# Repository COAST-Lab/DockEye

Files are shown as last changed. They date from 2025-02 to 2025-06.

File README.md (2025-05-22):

# Open Fluorometer

## About

This is the repository for an in-development, open-source, low-cost fluorometer for measuring water quality parameters. The current objective is measuring chlorophyll-*a* and turbidity,
though more parameters may be added in the future. This sensor uses a cuvette-based approach, similar to benchtop spectrofluorometers, rather than a truly in-situ one. The advantage of this approach is the ability to control ambient light while not strictly needing to be waterproof. Samples can be collected from the surface by hand or at depth using a Van Dorn sampler or CTD-Rosette.

This sensor continues the research from the now-deprecated https://github.com/COAST-Lab/Low-Cost-Multiparameter-Water-Quality-Sensor built using the Particle Argon microcontroller. 
The new version uses an ESP32-S3, which uses the Arduino IDE rather than the Particle Workbench.

The MOORE Foundation's SOCON (Sustained Ocean Color Observations from Nanosatellites) program funds this project.

## Introduction

This sensor is built using an Adafruit ESP32-S3 Feather microcontroller, an Adafruit Adalogger/RTC, an AS7341 light sensor, an AW9523 LED driver, a 430 nm blue LED, a 910 nm NIR LED, and a 3D printed enclosure. 
This repository currently contains firmware for flashing to the microcontroller and 3D printable design models for the enclosure, and scripts for data analysis, etc. This sensor is in active development, and this repository will be updated continuously as progress is made. 

## Parts

A list of parts can be found here:

- [ESP32-S3 Microcontroller](https://www.adafruit.com/product/5477)
- [Adalogger Datalogger/RTC](https://www.adafruit.com/product/2922)
- [AW9523 LED Driver](https://www.adafruit.com/product/4886)
- [AS7341 Light Sensor](https://www.adafruit.com/product/4698)
- [Blue LED](https://www.thorlabs.com/thorproduct.cfm?partnumber=LED430L)
- [NIR LED](https://www.thorlabs.com/thorproduct.cfm?partnumber=LED910L)

Additional parts include a soldering iron, solder, wire, a breadboard, access to a 3D printer, an SD card, a USB-C data cable, and hardware for assembling the sensor. 

A glass or quartz cuvette will be needed for calibrating and running samples. Because the chlorophyll-*a* calibration procedure is completed in acetone, plastic cuvettes are not advised. Acetone can dissolve some plastics, although certain plastics may be incompatible. The glass cuvettes that we are currently using are rather inexpensive, and can be found on Amazon [here](https://www.amazon.com/Fluorescence-Spectrophotometer-Cuvettes-pathlength-Fluorometer/dp/B07YDZ6K2B?crid=TBT16WYR38HM&dib=eyJ2IjoiMSJ9.Rx6TjeI6e-pFg3Mv68xtz28ZP_Q9hPI-yeQDbd4sN2l0LnT0KrBOkWjchOp21-8up7uFRnGXH4NQ6EaVXD32cu2CRUydlVmxSTyXF9Sp9oGG_GkgRuUTdxTE_vuw7iFTRlXKrGBJVSP3u1wZ12FmtyhuNQ71NkWIS9Gg2aIDsoQEjo3d2ZUMWSBvYHaW4YlxplcTskGwRPYe4TKxq8esrUAnyXS-2K3-_TNK5aQQeNM.WDhcMW94lNpOqJgwk2HZfrtGYfncKdvNy5RRSyoP6e8&dib_tag=se&keywords=glass+cuvettes&qid=1747334719&sprefix=glass+cuvettes%2Caps%2C126&sr=8-8). Ensure that any cuvettes purchased are specifically for fluorometry (with four transparent sides) and not for spectrophotometers, as those only have two transparent sides. These are incompatible with this design, as the LEDs in this design are placed at a 90-degree angle from the light detector. 

3D print files can be found [here](https://github.com/COAST-Lab/Open-Fluorometer/tree/main/Hardware/Housing).

## Wiring Instructions

Instructions for assembly will be added soon. For now, here is a simple explanation on how to wire the parts together:

- Solder the included male headers onto the corresponding pins on the ESP-32
- Solder the stacking headers onto corresponding pins on the Adalogger
- Solder/insert (depending on type) pins into breadboard
- Add a jumper wire from 3.3V and GND to +/-
- Solder the following pins on the AW9523 to the corresponding pins on the ESP32-S3
  - VIN to +
  - GND to -
  - SCL to SCL
  - SDA to SDA
- Solder the following pins on the AS7341 to the corresponding pins on the ESP32-S3
  - VIN to +
  - GND to -
  - SCL to SCL
  - SDA to SDA
- Solder the Blue LED to + and AW9523 Pin 10
- Solder the NIR LED to + and AW9523 Pin 0

Instructions for mounting the LEDs and light sensor to the cuvette holder will be added soon.

## Data Analysis

Scripts for data analysis and data files can be found [here](https://github.com/COAST-Lab/Open-Fluorometer/tree/main/Data%20Analysis).

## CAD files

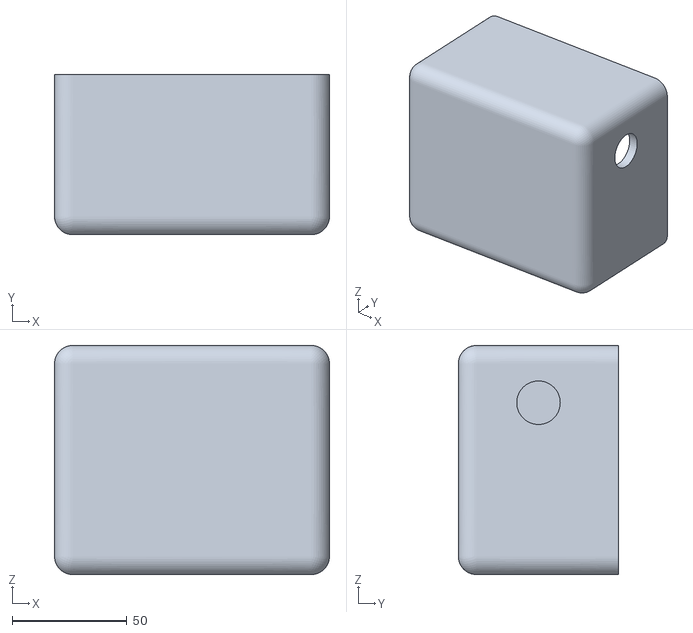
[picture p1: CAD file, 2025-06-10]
Hardware/Housing/Open-Fluorometer-Main-Housing v7.stl
120.0 x 70.0 x 100.0

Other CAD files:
Hardware/Housing/Open-Fluorometer-Main-Housing v9.stl
Hardware/Housing/Open-Fluorometer-Main-Housing v8.stl
Hardware/Housing/Open-Fluorometer-Lid v2.f3d
Hardware/Housing/Open-Fluorometer-Main-Housing v4.f3d

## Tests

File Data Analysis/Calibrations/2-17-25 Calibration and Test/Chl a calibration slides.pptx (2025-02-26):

## Chlorophyll-a calibration curve

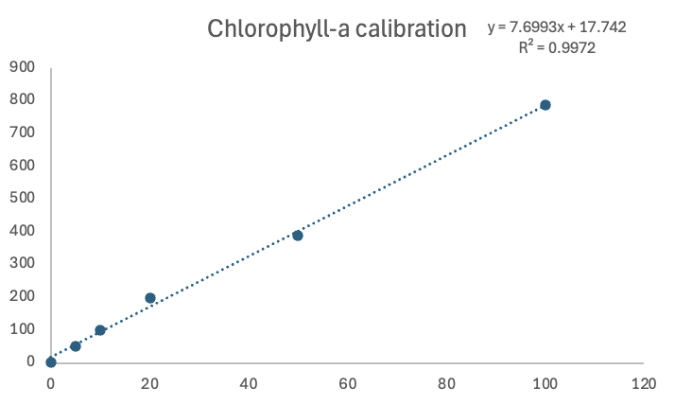
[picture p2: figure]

- Dilutions made from a stock solution measured at 297.7 ug/L
- Completed serial dilution from 100 to 5 ug/L in 90% acetone
- Vortexed stocks and standards before spiking

Concentration (ug/L) | Counts
100 | 788.625
50 | 389.1875
20 | 199.75
10 | 99.4375
5 | 50.75
0 | 3.0625

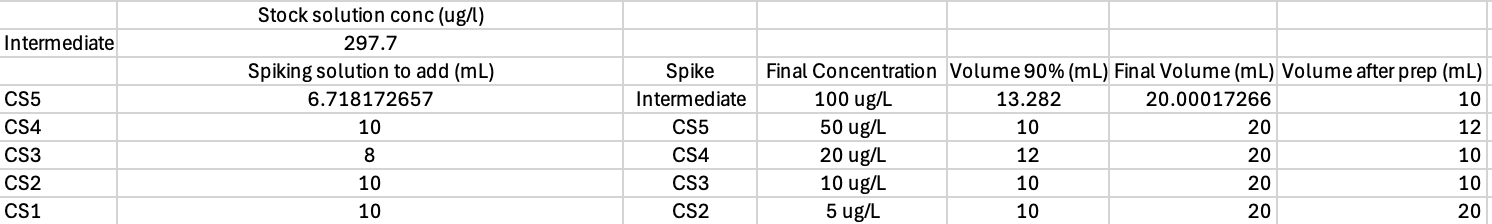
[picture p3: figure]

## Field validation test

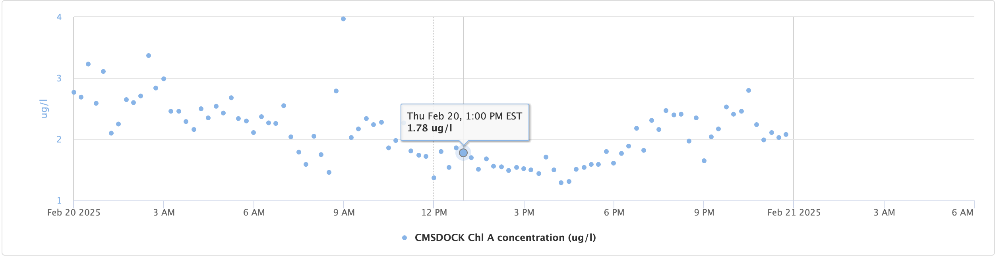
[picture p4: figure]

- Sampling location close to CORMP EXO2
- 1.78 ug/L measurement from CORMP
- Measurement taken on the surface in an amber bottle
  - CORMP measurements deeper
- 17.89 ug/L average on OF
  - Factor of 10 difference, calculation error or sensor issue?

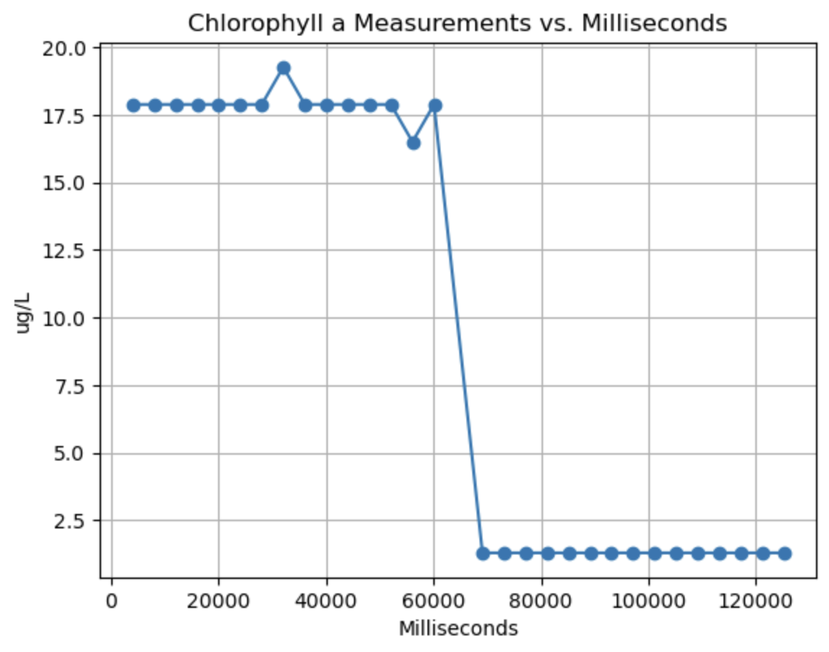
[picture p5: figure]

## Potential causes of discrepancy

- Calculations
  - Spreadsheet for trichromatic chlorophyll method may have calculation mistake
  - Problem with calibration curve calculations
  - Problem with python script
- Environmental factors
  - Acetone vs seawater
  - Photochemical quenching in seawater
  - EXO2 in a slightly different place at a different depth (slightly)
- Sensor sensitivity issue

## Solutions

1. Check all calculations again and have Phil double check them
2. Calibrate Dr. Loh’s Horiba and test standards on there to determine if it agrees with the spectrophotometer or the OF
3. Use Van Dorn sampler to sample in the same place and depth as the EXO2
4. Make chlorophyll standards using CMS highly filtered seawater rather than acetone

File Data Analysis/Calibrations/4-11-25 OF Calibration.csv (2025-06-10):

Date and Time | ASTEP | ATIME | GAIN | LED Status | LED Intensity | Test | Seconds | Milliseconds | Type | F1 (Basic) | F2 (Basic) | F3 (Basic) | F4 (Basic) | F5 (Basic) | F6 (Basic) | F7 (Basic) | F8 (Basic) | Clear (Basic) | NIR (Basic) | Type | F1 (Raw) | F2 (Raw) | F3 (Raw) | F4 (Raw) | F5 (Raw) | F6 (Raw) | F7 (Raw) | F8 (Raw) | Clear (Raw) | NIR (Raw) | Measurement Type
2104/5/32 (Monday) 30:7:22 | 999 | 255 | 9 | LED Status | LED Intensity | 6 | 21 | 21491 | BASIC COUNTS | 0 | 0 | 0 | 0 | 0 | 0 | 0 | 0 | 0 | 0 | RAW VALUES | 134 | 592 | 57 | 19 | 14 | 17 | 16 | 11 | 562 | 0 | chlorophyll a
2104/5/32 (Monday) 30:7:26 | 999 | 255 | 9 | LED Status | LED Intensity | 6 | 25 | 25481 | BASIC COUNTS | 0 | 0 | 0 | 0 | 0 | 0 | 0 | 0 | 0 | 0 | RAW VALUES | 131 | 589 | 57 | 20 | 13 | 16 | 15 | 11 | 559 | 0 | chlorophyll a
2104/5/32 (Monday) 30:7:30 | 999 | 255 | 9 | LED Status | LED Intensity | 6 | 29 | 29470 | BASIC COUNTS | 0 | 0 | 0 | 0 | 0 | 0 | 0 | 0 | 0 | 0 | RAW VALUES | 131 | 587 | 58 | 19 | 14 | 18 | 15 | 10 | 557 | 0 | chlorophyll a
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

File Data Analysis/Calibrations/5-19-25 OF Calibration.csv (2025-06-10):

Date and Time | ASTEP | ATIME | GAIN | LED Status | LED Intensity | Test | Seconds | Milliseconds | Type | F1 (Basic) | F2 (Basic) | F3 (Basic) | F4 (Basic) | F5 (Basic) | F6 (Basic) | F7 (Basic) | F8 (Basic) | Clear (Basic) | NIR (Basic) | Type | F1 (Raw) | F2 (Raw) | F3 (Raw) | F4 (Raw) | F5 (Raw) | F6 (Raw) | F7 (Raw) | F8 (Raw) | Clear (Raw) | NIR (Raw) | Measurement Type | Average | Blank
2104/5/32 (Monday) 30:6:17 | 999 | 255 | 9 | LED Status | LED Intensity | 6 | 17 | 17056 | BASIC COUNTS | 0 | 0 | 0 | 0 | 0 | 0 | 0 | 0 | 0 | 0 | RAW VALUES | 109 | 528 | 46 | 6 | 3 | 7 | 10 | 10 | 466 | 0 | chlorophyll a | 11.125 |  | 11.125 | 0
2104/5/32 (Monday) 30:6:21 | 999 | 255 | 9 | LED Status | LED Intensity | 6 | 21 | 21046 | BASIC COUNTS | 0 | 0 | 0 | 0 | 0 | 0 | 0 | 0 | 0 | 0 | RAW VALUES | 108 | 529 | 46 | 5 | 2 | 8 | 10 | 10 | 466 | 0 | chlorophyll a |  |  | 46.3125 | 5
2104/5/32 (Monday) 30:6:25 | 999 | 255 | 9 | LED Status | LED Intensity | 6 | 25 | 25034 | BASIC COUNTS | 0 | 0 | 0 | 0 | 0 | 0 | 0 | 0 | 0 | 0 | RAW VALUES | 108 | 527 | 47 | 6 | 2 | 8 | 10 | 10 | 465 | 0 | chlorophyll a |  |  | 90.6875 | 10
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

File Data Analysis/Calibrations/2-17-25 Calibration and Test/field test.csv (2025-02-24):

Date and Time | ASTEP | ATIME | GAIN | LED Status | LED Intensity | Test | Seconds | Milliseconds | Type | F1 (Basic) | F2 (Basic) | F3 (Basic) | F4 (Basic) | F5 (Basic) | F6 (Basic) | F7 (Basic) | F8 (Basic) | Clear (Basic) | NIR (Basic) | Type | F1 (Raw) | F2 (Raw) | F3 (Raw) | F4 (Raw) | F5 (Raw) | F6 (Raw) | F7 (Raw) | F8 (Raw) | Clear (Raw) | NIR (Raw) | Measurement Type
2104/5/32 (Monday) 30:7:5 | 999 | 255 | 8 | LED Status | LED Intensity | 6 | 5 | 5460 | BASIC COUNTS | 0 | 0 | 0 | 0 | 0 | 0 | 0 | 0 | 0 | 0 | RAW VALUES | 87 | 342 | 27 | 7 | 5 | 8 | 7 | 7 | 324 | 0 | chlorophyll a
2104/5/32 (Monday) 30:7:9 | 999 | 255 | 8 | LED Status | LED Intensity | 6 | 9 | 9450 | BASIC COUNTS | 0 | 0 | 0 | 0 | 0 | 0 | 0 | 0 | 0 | 0 | RAW VALUES | 83 | 334 | 27 | 7 | 5 | 8 | 7 | 6 | 317 | 0 | chlorophyll a
2104/5/32 (Monday) 30:7:13 | 999 | 255 | 8 | LED Status | LED Intensity | 6 | 13 | 13440 | BASIC COUNTS | 0 | 0 | 0 | 0 | 0 | 0 | 0 | 0 | 0 | 0 | RAW VALUES | 83 | 333 | 27 | 6 | 4 | 7 | 7 | 6 | 318 | 0 | chlorophyll a
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

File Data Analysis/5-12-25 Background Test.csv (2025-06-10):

Date and Time | ASTEP | ATIME | GAIN | LED Status | LED Intensity | Test | Seconds | Milliseconds | Type | F1 (Basic) | F2 (Basic) | F3 (Basic) | F4 (Basic) | F5 (Basic) | F6 (Basic) | F7 (Basic) | F8 (Basic) | Clear (Basic) | NIR (Basic) | Type | F1 (Raw) | F2 (Raw) | F3 (Raw) | F4 (Raw) | F5 (Raw) | F6 (Raw) | F7 (Raw) | F8 (Raw) | Clear (Raw) | NIR (Raw) | Measurement Type
Date and Time | ASTEP | ATIME | GAIN | LED Status | LED Intensity | Test | Seconds | Milliseconds | Type | F1 (Basic) | F2 (Basic) | F3 (Basic) | F4 (Basic) | F5 (Basic) | F6 (Basic) | F7 (Basic) | F8 (Basic) | Clear (Basic) | NIR (Basic) | Type | F1 (Raw) | F2 (Raw) | F3 (Raw) | F4 (Raw) | F5 (Raw) | F6 (Raw) | F7 (Raw) | F8 (Raw) | Clear (Raw) | NIR (Raw) | Measurement Type
2112/5/32 (Thursday) 30:7:9 | 999 | 255 | 9 | LED Status | LED Intensity | 6 | 8 | 8680 | BASIC COUNTS | 0 | 0 | 0 | 0 | 0 | 0 | 0 | 0 | 0 | 0 | RAW VALUES | 130 | 627 | 54 | 7 | 3 | 9 | 9 | 5 | 542 | 0 | chlorophyll a
2112/5/32 (Thursday) 30:7:14 | 999 | 255 | 9 | LED Status | LED Intensity | 6 | 13 | 13667 | BASIC COUNTS | 0 | 0 | 0 | 0 | 0 | 0 | 0 | 0 | 0 | 0 | RAW VALUES | 130 | 627 | 55 | 6 | 3 | 10 | 9 | 5 | 544 | 0 | chlorophyll a
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

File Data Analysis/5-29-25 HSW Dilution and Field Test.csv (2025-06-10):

Date and Time | ASTEP | ATIME | GAIN | LED Status | LED Intensity | Test | Seconds | Milliseconds | Type | F1 (Basic) | F2 (Basic) | F3 (Basic) | F4 (Basic) | F5 (Basic) | F6 (Basic) | F7 (Basic) | F8 (Basic) | Clear (Basic) | NIR (Basic) | Type | F1 (Raw) | F2 (Raw) | F3 (Raw) | F4 (Raw) | F5 (Raw) | F6 (Raw) | F7 (Raw) | F8 (Raw) | Clear (Raw) | NIR (Raw) | Measurement Type
2104/5/32 (Monday) 30:22:27 | 999 | 255 | 9 | LED Status | LED Intensity | 6 | 11 | 11234 | BASIC COUNTS | 0 | 0 | 0 | 0 | 0 | 0 | 0 | 0 | 0 | 0 | RAW VALUES | 151 | 686 | 58 | 8 | 3 | 12 | 11 | 7 | 611 | 0 | Chlorophyll-a |  | 0.37 | 0
2104/5/32 (Monday) 30:22:30 | 999 | 255 | 9 | LED Status | LED Intensity | 6 | 14 | 14204 | BASIC COUNTS | 0 | 0 | 0 | 0 | 0 | 0 | 0 | 0 | 0 | 0 | RAW VALUES | 149 | 685 | 59 | 8 | 4 | 11 | 11 | 8 | 608 | 0 | Chlorophyll-a | DIW
2104/5/32 (Monday) 30:22:33 | 999 | 255 | 9 | LED Status | LED Intensity | 6 | 17 | 17173 | BASIC COUNTS | 0 | 0 | 0 | 0 | 0 | 0 | 0 | 0 | 0 | 0 | RAW VALUES | 148 | 686 | 58 | 9 | 4 | 11 | 11 | 6 | 609 | 0 | Chlorophyll-a |  | 0.37 | 0
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

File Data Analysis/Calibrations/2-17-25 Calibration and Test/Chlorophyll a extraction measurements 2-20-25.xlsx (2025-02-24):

 | 10 cm cell in 90% acetone |  |  |  | Baseline corrected and corrected to 1 cm pathlength |  |  | Jeffrey and Humphrey's Trichromatic EPA methods | Chazaux, Schiphorst, Lazzari and Caffarri 2022 doi: 10.1111/tpj.15643 | Jeffrey and Humphrey's Trichromatic EPA methods | Chazaux, Schiphorst, Lazzari and Caffarri 2022 doi: 10.1111/tpj.15643 | JGOFS | Jeffrey and Humphrey's Trichromatic EPA methods | Chazaux, Schiphorst, Lazzari and Caffarri 2022 doi: 10.1111/tpj.15643 | JGOFS
 | 750nm | 664nm | 647nm | 630nm | 664nm (corr) | 647nm(corr) | 630nm(corr) | Chl a mg/L |  | Chl a µg/L |  |  | Average conc. µg/L
 | 0.0121 | 0.0631 | 0.0339 | 0.0302 | 0.0051 | 0.0022 | 0.0018 | 0.057 | 0.056 | 57.2 | 56.4 | 58.2
 | 0.0149 | 0.0634 | 0.0346 | 0.0311 | 0.0049 | 0.0020 | 0.0016 | 0.055 | 0.054 | 54.6 | 53.9 | 55.3
 | -0.0054 | 1.2566 | 0.5437 | 0.2618 | 0.1262 | 0.0549 | 0.0267 | 1.413 | 1.392 | 1413.0 | 1392.2 | 1439.5
1 | -0.0039 | 0.2763 | 0.1206 | 0.0587 | 0.0280 | 0.0124 | 0.0063 | 0.313 | 0.308 | 313.4 | 308.4 | 319.6
2 | -0.0054 | 0.2796 | 0.1198 | 0.0573 | 0.0285 | 0.0125 | 0.0063 | 0.319 | 0.314 | 318.9 | 314.1 | 325.1
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

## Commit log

2024-11-22 Added housing files
    Added .f3d files for the main housing and lid
    [Open-Fluorometer-Lid v1.f3d, Open-Fluorometer-Main-Housing v4.f3d]
2024-11-25 Fixed misaligned hole
    Fixed a misaligned hole on the lid.
    [Open-Fluorometer-Lid v1.f3d, Open-Fluorometer-Lid v2.f3d]
2025-02-24 Added data analysis files
    Added calibration information and data analysis
    [Chlorophyll a extraction measurements 2-20-25.xlsx, field test.csv]
2025-05-22 Updated firmware
    Updated firmware to 256x gain, added a report that averages measurements, subtracts baseline, and calibrates measurement (must enter calibration curve). Also added a loading bar to see at what point 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
2025-06-10 Added data files
    [3-10-25 Field Test.csv, 3-14-25 Field Test.csv, 3-21-25 Field Test.csv, 3-24-25 Field Test.csv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]
